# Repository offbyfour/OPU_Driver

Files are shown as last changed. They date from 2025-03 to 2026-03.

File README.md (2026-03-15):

# Blu-Ray Lithography
## Introduction
This is the project page for a lithography system based on repurposing Blu-Ray drives. The initial goal is to reach a feature size of at least 500nm (2x the Blu-ray laser spot size). As a stretch goal, we would like to also use the sled and spindle motors as high speed nano-positioners and to spin coat and cure photo-resin.

## Safety
✓ Safety goggles/glasses are absolutely necessary.
A laser dot contains a large amount of energy in such a small space, in the form of light. Your eyes are extremely sensitive to light, and a direct exposure to this very dense energy light for less than a second will blind you for life. We can prevent this by wearing a special type of light filtering glasses, somewhat like the way sunglasses work. But, sunglasses will not work as laser safety glasses. These glasses need to be coated for the correct wavelength. Do not purchase any laser safety glasses under $30, buy from an authorized and reputable seller such as survival lasers. $5 lenses from China will not be sufficient, and have been proven unsafe.

Currently Recommended: https://www.amazon.com/Tool-Klean-Safety-Glasses-Protection/dp/B081BHTJT8/ref=sr_1_5

✓ Be fully aware of what you are pointing at.
With a massive amount of light comes the heat as well. Lasers higher than Class IV (>500mW) burn certain objects very easily, lower powers do burn as well but not as intensely. Lasers like this can most definitely burn furniture such as carpet and couches, hardwood floors, curtains, walls etc. You need to make sure that you are not burning anything against your desire. If the heat build up in an object from a laser is sufficient enough, the object could be set on fire.

✓ Keep in mind of any dangerous objects/surfaces.
Look out for anything noticeably reflective/smooth such as a mirror, polished metal, or even something smooth like a desk. The last thing you want is a laser beam reflected back at you into your eye. Even with safety goggles/glasses, you should not take a chance. Something else dangerous that you need to look out for are flammable items, a high powered laser can easily ignite a match or alcohol. CAREFUL WITH WINDOWS - None are 100% transparent, and WILL reflect a solid beam back towards you, this goes for any type of glass at all. All reflected beams are also a danger and this is no exception. Windows are also a bad thing to be pointing a laser through, you don't know exactly where/what you'll hit.

__________________________________________________

Be careful with lasers, treat them like a loaded gun. It is very easy to create dangerous situations with a laser if you're not careful, be responsible and eliminate that possibility!
Source: laserpointerforums.com

## Project Status

 

Right now, the first project for this technology (Lithography Spinner V1) is in the research/idea stage. See work in progress page for details on upcoming tasks if you want to contribute.

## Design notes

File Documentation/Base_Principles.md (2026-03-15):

<details>
  <summary>STED Lithography (reaching 100nm and below)</summary>
1.STED Microscopy
	
https://www.youtube.com/watch?v=1pgpzHao1c0

2.Two-beam OBL utilizes a doughnut-shaped inhibition beam to inhibit the photopolymerization triggered by the writing beam at the doughnut ring leading to reduced feature size and improved resolution 

https://www.nature.com/articles/ncomms3061

3.Super-resolved critical dimensions in far-field I-line photolithography

https://www.spiedigitallibrary.org/journals/journal-of-micro-nanolithography-mems-and-moems/volume-18/issue-1/013505/Super-resolved-critical-dimensions-in-far-field-I-line-photolithography/10.1117/1.JMM.18.1.013505.short

4.Possible STED Architecture

Diagram of BSM. The fluorescence signal passes through multimode fiber B7 and is collimated by collimator lens B8 and narrowband emission filter B9. D1, laser diode; D2, beam splitter; D3, collimator lens; D4, dichroic filter; D5, photodiode; D6, objective lens (NA: 0.6); D7, Al-coated address pattern; B1, blue laser diode; B2, B3, beam splitters; B4, collimator lens; B5, dichroic filter; B6, 4.34 mm focal lens; B10, objective lens (NA: 0.85); B11, lens holder. B12, cover glass; B13, collimator astigmatic plate; B14, photodetector. (https://pmc.ncbi.nlm.nih.gov/articles/PMC6066758/)

</details>

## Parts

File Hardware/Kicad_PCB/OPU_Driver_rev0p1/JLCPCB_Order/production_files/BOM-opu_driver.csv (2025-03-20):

Comment | Designator | Footprint | LCSC | Quantity
1kΩ | R14,R28 | R_0402 | C11702 | 2
ESD9X3.3ST5G | D4 | SOD-923_L0.8-W0.6-LS1.0-RD | C130456 | 1
10nF | C47,C48,C49,C50,C51,C52,C53,C54,C55,C56,C57,C58,C59,C61,C72,C73 | C_0402 | C15195 | 16
TLV62569DRLR | U10,U11 | SOT-563_L1.6-W1.2-P0.50-LS1.6-BL | C163217 | 2
RC0402FR-071K8L | R27 | R0402 | C163481 | 1
0Ω | R23,R24,R25 | R_0402 | C17168 | 3
0Ω | R38,R39 | R_0603 | C21189 | 2
White | D9 | D_0603 | C2290 | 1
360kΩ | R19 | R_0603 | C23146 | 1
750kΩ | R6 | R_0603 | C23240 | 1
82kΩ | R22 | R_0603 | C23254 | 1
100Ω | R26 | R_0402 | C25076 | 1
33Ω | R44,R45,R46 | R_0402 | C25105 | 3
51Ω | R29,R30 | R_0402 | C25125 | 2
1Ω | R31,R32,R33,R34 | R_0805 | C25271 | 4
X1E0000210295 | X1 | CRYSTAL-SMD_4P-L3.2-W2.5-BL | C255930 | 1
100kΩ | R21 | R_0402 | C25741 | 1
10kΩ | R10,R20,R35,R41,R42,R43 | R_0402 | C25744 | 6
120kΩ | R18 | R_0402 | C25750 | 1
150kΩ | R5 | R_0402 | C25755 | 1
200kΩ | R1 | R_0402 | C25764 | 1
4.7kΩ | R11,R13,R15,R16,R17,R3,R4,R40,R7,R8,R9 | R_0402 | C25900 | 11
MAX1304ECM+T | U6 | TQFP-48_L7.0-W7.0-P0.50-LS9.0-BL | C2670670 | 1
GT-USB-7018 | USB1 | TYPE-C-SMD_GT-USB-7018 | C2762978 | 1
1uF | C4,C81,C90 | C_0805 | C28323 | 3
CH569W | U1 | QFN-68_L8.0-W8.0-P0.40-BL-EP5.5 | C2857462 | 1
HD3SS3220IRNHT | U2 | WQFN-30_L4.5-W2.5-P0.4-BL-EP | C2876685 | 1
DIP Switch x 2 | S1 | SW-SMD_218-2LPSTRF | C2961921 | 1
4.7uF | C100,C101,C102,C103,C104,C105,C106,C107,C108,C3,C5,C79,C80,C82,C83,C84,C85,C86,C87,C88,C89,C95,C96,C97,C98,C99 | C_1206 | C29823 | 26
Green | D7 | D_0603 | C2986059 | 1
6pF | C117 | C_0402 | C30274 | 1
100nF | C10,C109,C11,C110,C111,C112,C113,C114,C115,C116,C118,C119,C12,C120,C121,C122,C123,C124,C125,C126,C127,C128,C13,C14,C15,C16,C17,C18,C19,C20,C21,C22,C23,C24,C25,C26,C27,C28,C29,C30,C31,C32,C33,C34,C35,C36,C37,C38,C39,C40,C41,C42,C43,C44,C45,C46,C60,C62,C63,C64,C65,C67,C68,C69,C70,C74,C75,C76,C77,C78,C8,C9,C92 | C_0402 | C307331 | 73
Tactile Button, 160gf | S2 | SW-SMD_4P-L5.1-W5.1-P3.70-LS6.5-TL-2 | C318884 | 1
10pF | C6,C7,C93,C94 | C_0402 | C32949 | 4
2kΩ | R36,R37 | R_0402 | C4109 | 2
TPD1S414YZR | U3 | DSBGA-12_L1.9-W1.4-R3-C4-P0.40-TL | C411873 | 1
ZX-PM1.0-2-20PU-W | H1 | HDR-SMD_40P-P1.00-V-F-R2-C20-LS3.8 | C41369836 | 1
LM3880MF-1AA/NOPB | U13 | SOT-23-6_L2.9-W1.6-P0.95-LS2.8-BR | C486059 | 1
2.2uF | C1,C2,C66,C71,C91 | C_1206 | C50254 | 5
CR2512J1R220G | R12 | R2512 | C5381546 | 1
PMEG6010AESBYL | D5,D6 | X1SON-2_L1.0-W0.6-P0.65-RD | C552929 | 2
BLM15EX331SN1D | L1 | L0402 | C596498 | 1
NCP115CMX250TCG | U9 | XDFN-4_L1.0-W1.0-P0.65-BL-EP | C603508 | 1
ESD8004MUTAG | D1,D2,D3 | UDFN-10_L2.5-W1.0-P0.50-BL | C605399 | 3
EPC21603 | U12 | BGA-6_L1.5-W1.0-P0.50-TL | C6191277 | 1
TPIC2010RDFDRG4 | U8 | HTSSOP-56_L14.0-W6.0-P0.50-LS8.1-BL-EP | C702134 | 1
MAX40025CAWT+T | U5 | WLP-6_L1.2-W0.8-R2-C3-P0.40-TL_MAX40111ANT | C7451830 | 1
2N7002 | Q1,Q2 | Q_SOT-23 | C8545 | 2
LQM21PN2R2NGCD | L2,L3 | L0805 | C86089 | 2
TestPoint | TP11 | TestPoint_Pad_D1.0mm |  | 1
LMK3H0102A014RERT | U7 | TQFN16_RER_TEX |  | 1
TestPoint | TP6 | TestPoint_Pad_D1.0mm |  | 1
TestPoint | TP8 | TestPoint_Pad_D1.0mm |  | 1
TestPoint | TP10 | TestPoint_Pad_D1.0mm |  | 1
TestPoint | TP7 | TestPoint_Pad_D1.0mm |  | 1
TestPoint | TP9 | TestPoint_Pad_D1.0mm |  | 1
LFE5U-25F-8MG285C | U4 | csBGA285 |  | 1
TestPoint | TP1 | TestPoint_Pad_D1.0mm |  | 1
TestPoint | TP5 | TestPoint_Pad_D1.0mm |  | 1
TestPoint | TP4 | TestPoint_Pad_D1.0mm |  | 1
TestPoint | TP2 | TestPoint_Pad_D1.0mm |  | 1
TestPoint | TP3 | TestPoint_Pad_D1.0mm |  | 1

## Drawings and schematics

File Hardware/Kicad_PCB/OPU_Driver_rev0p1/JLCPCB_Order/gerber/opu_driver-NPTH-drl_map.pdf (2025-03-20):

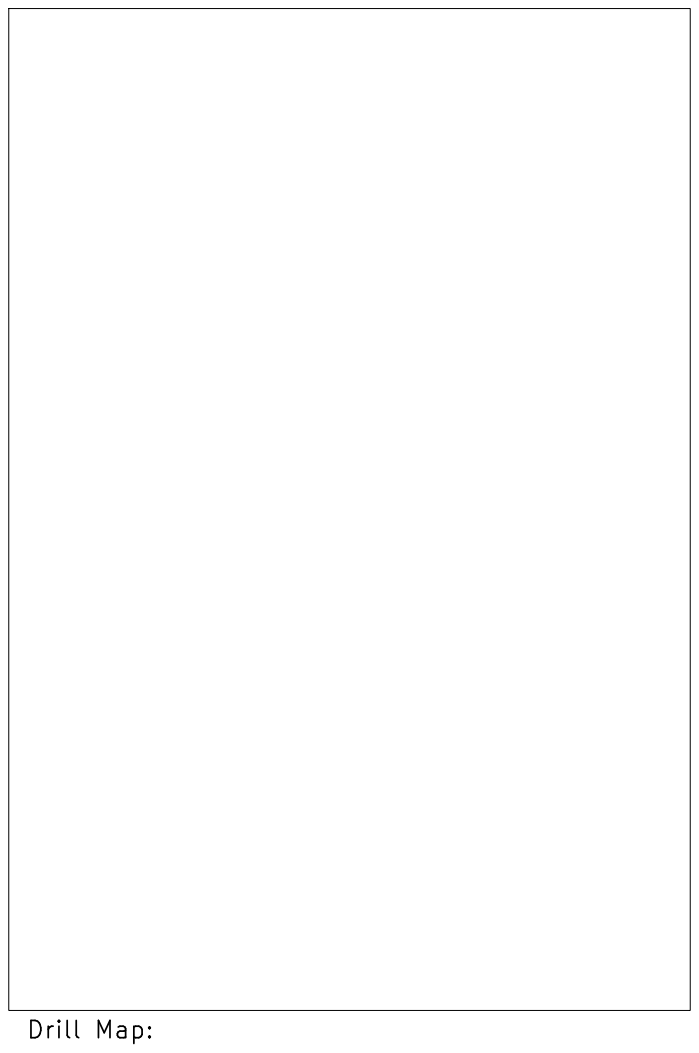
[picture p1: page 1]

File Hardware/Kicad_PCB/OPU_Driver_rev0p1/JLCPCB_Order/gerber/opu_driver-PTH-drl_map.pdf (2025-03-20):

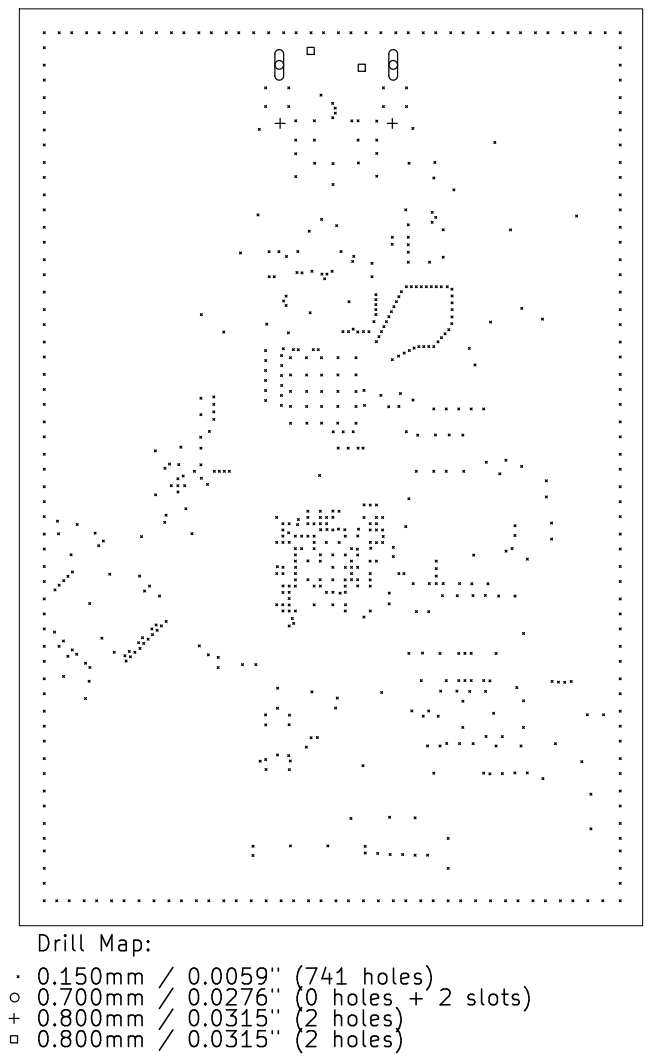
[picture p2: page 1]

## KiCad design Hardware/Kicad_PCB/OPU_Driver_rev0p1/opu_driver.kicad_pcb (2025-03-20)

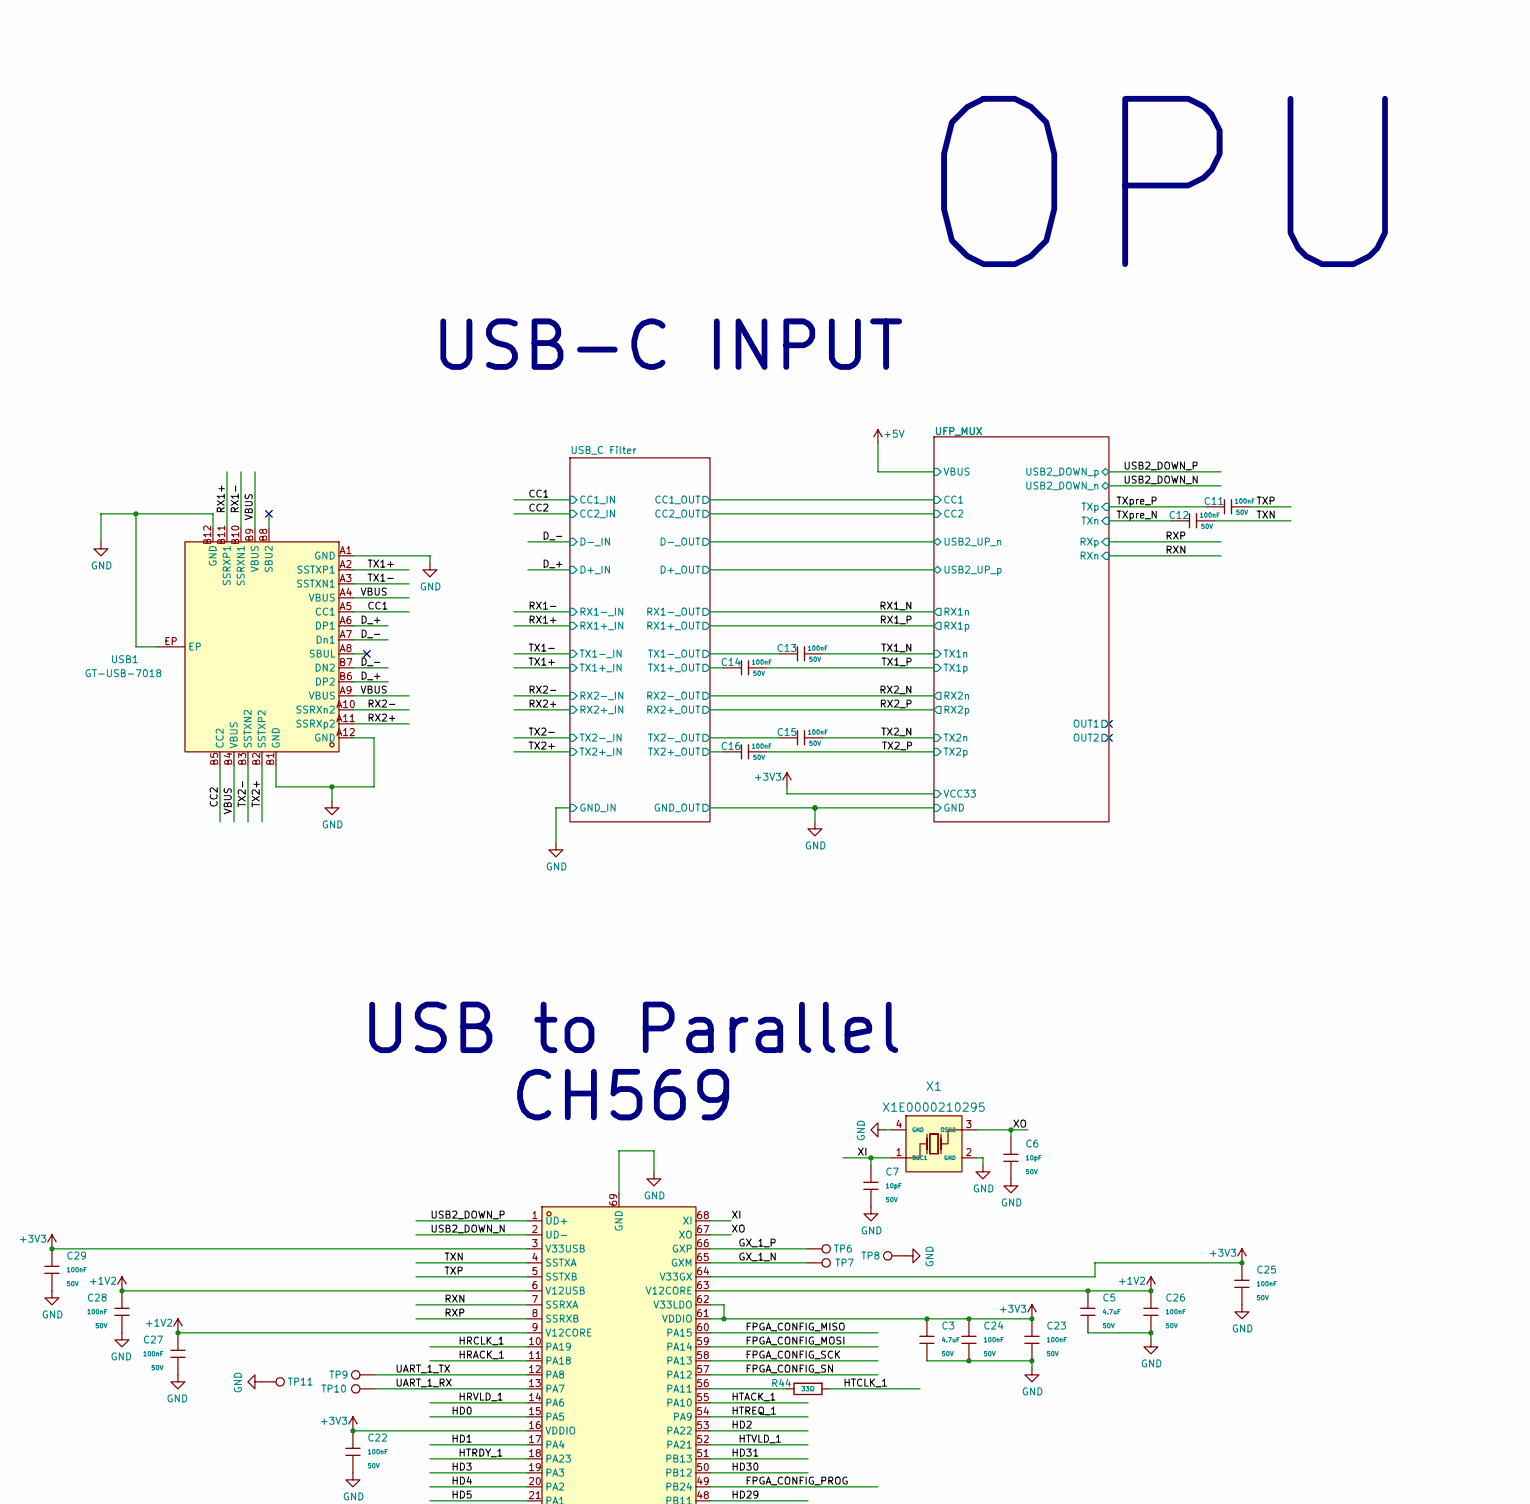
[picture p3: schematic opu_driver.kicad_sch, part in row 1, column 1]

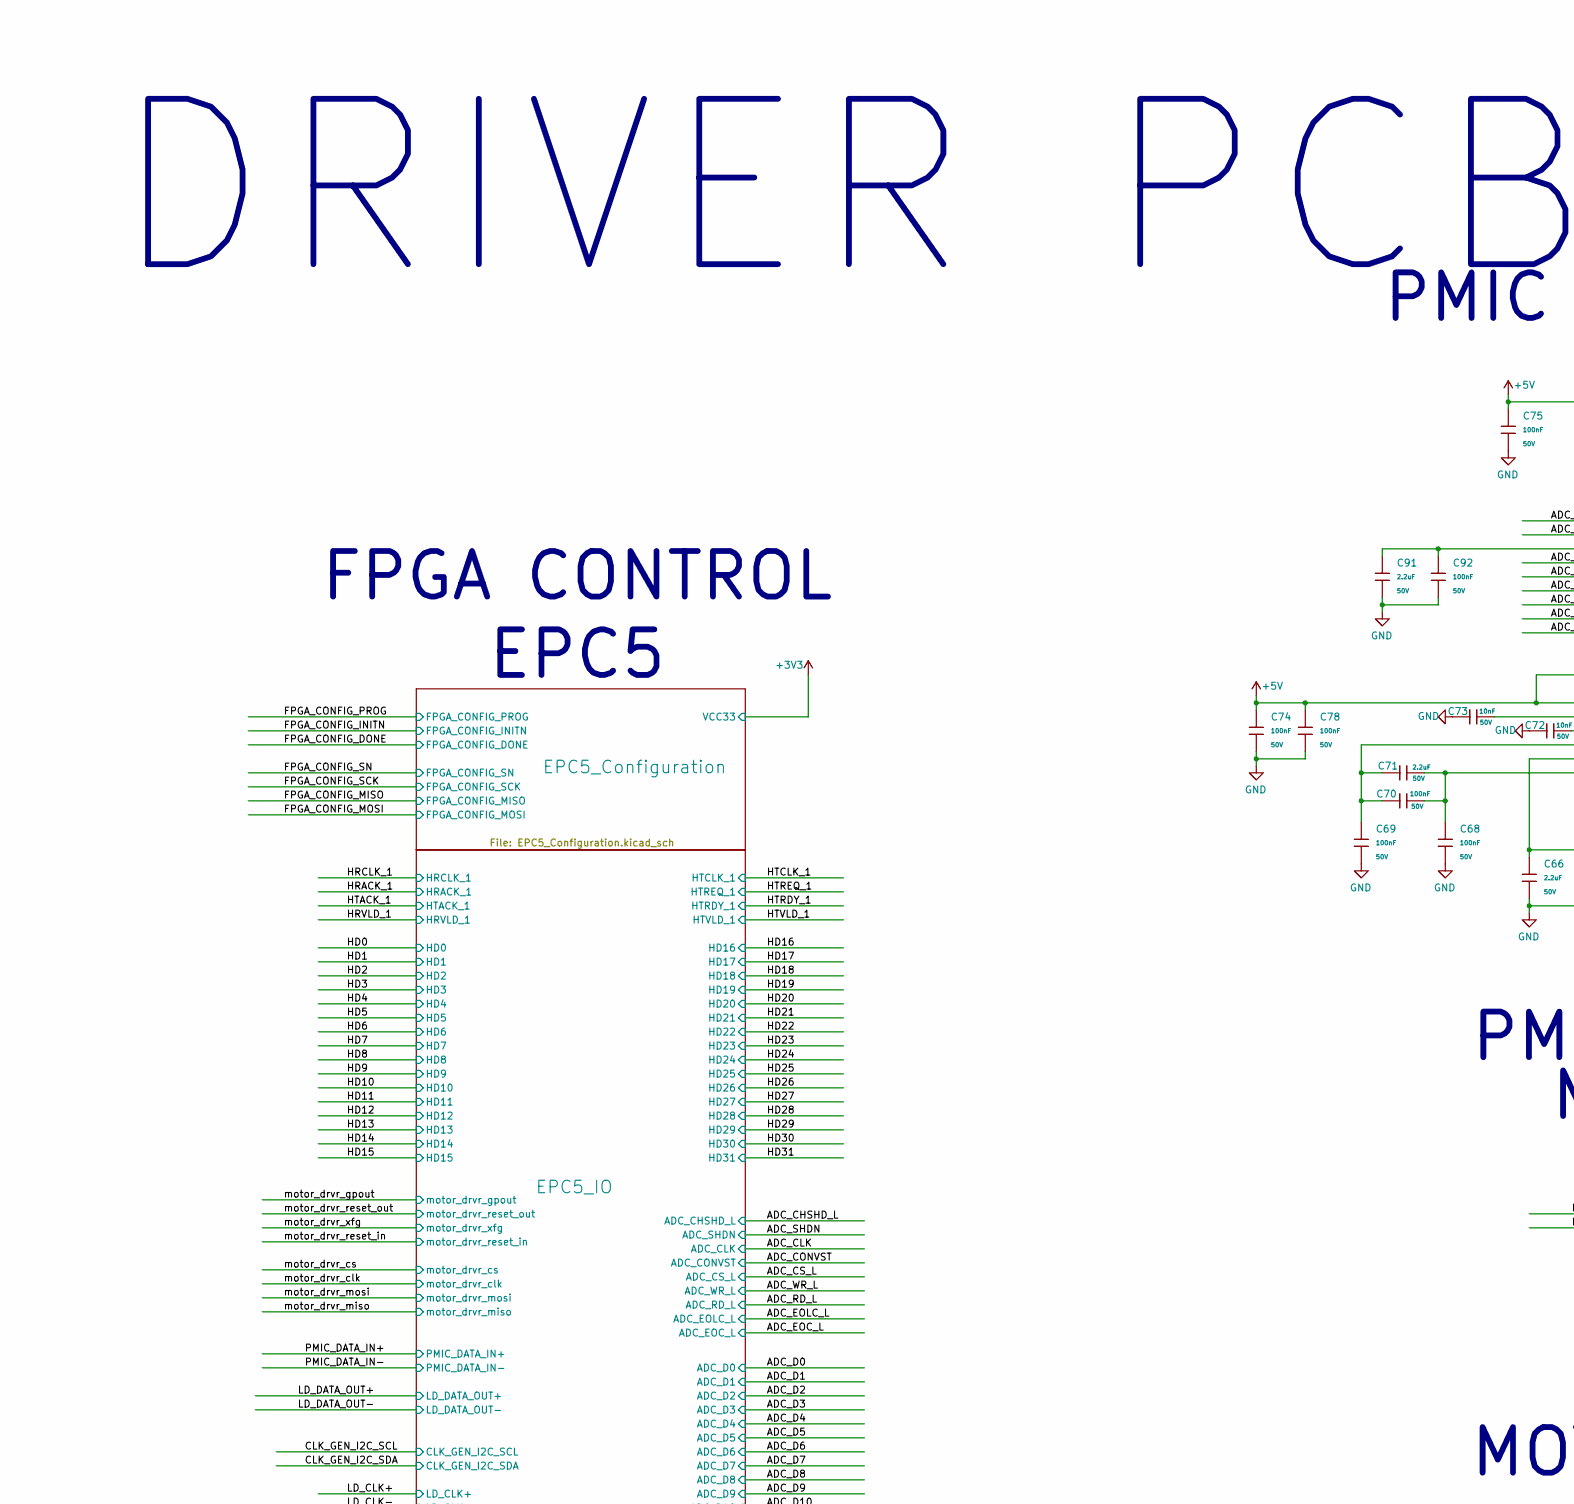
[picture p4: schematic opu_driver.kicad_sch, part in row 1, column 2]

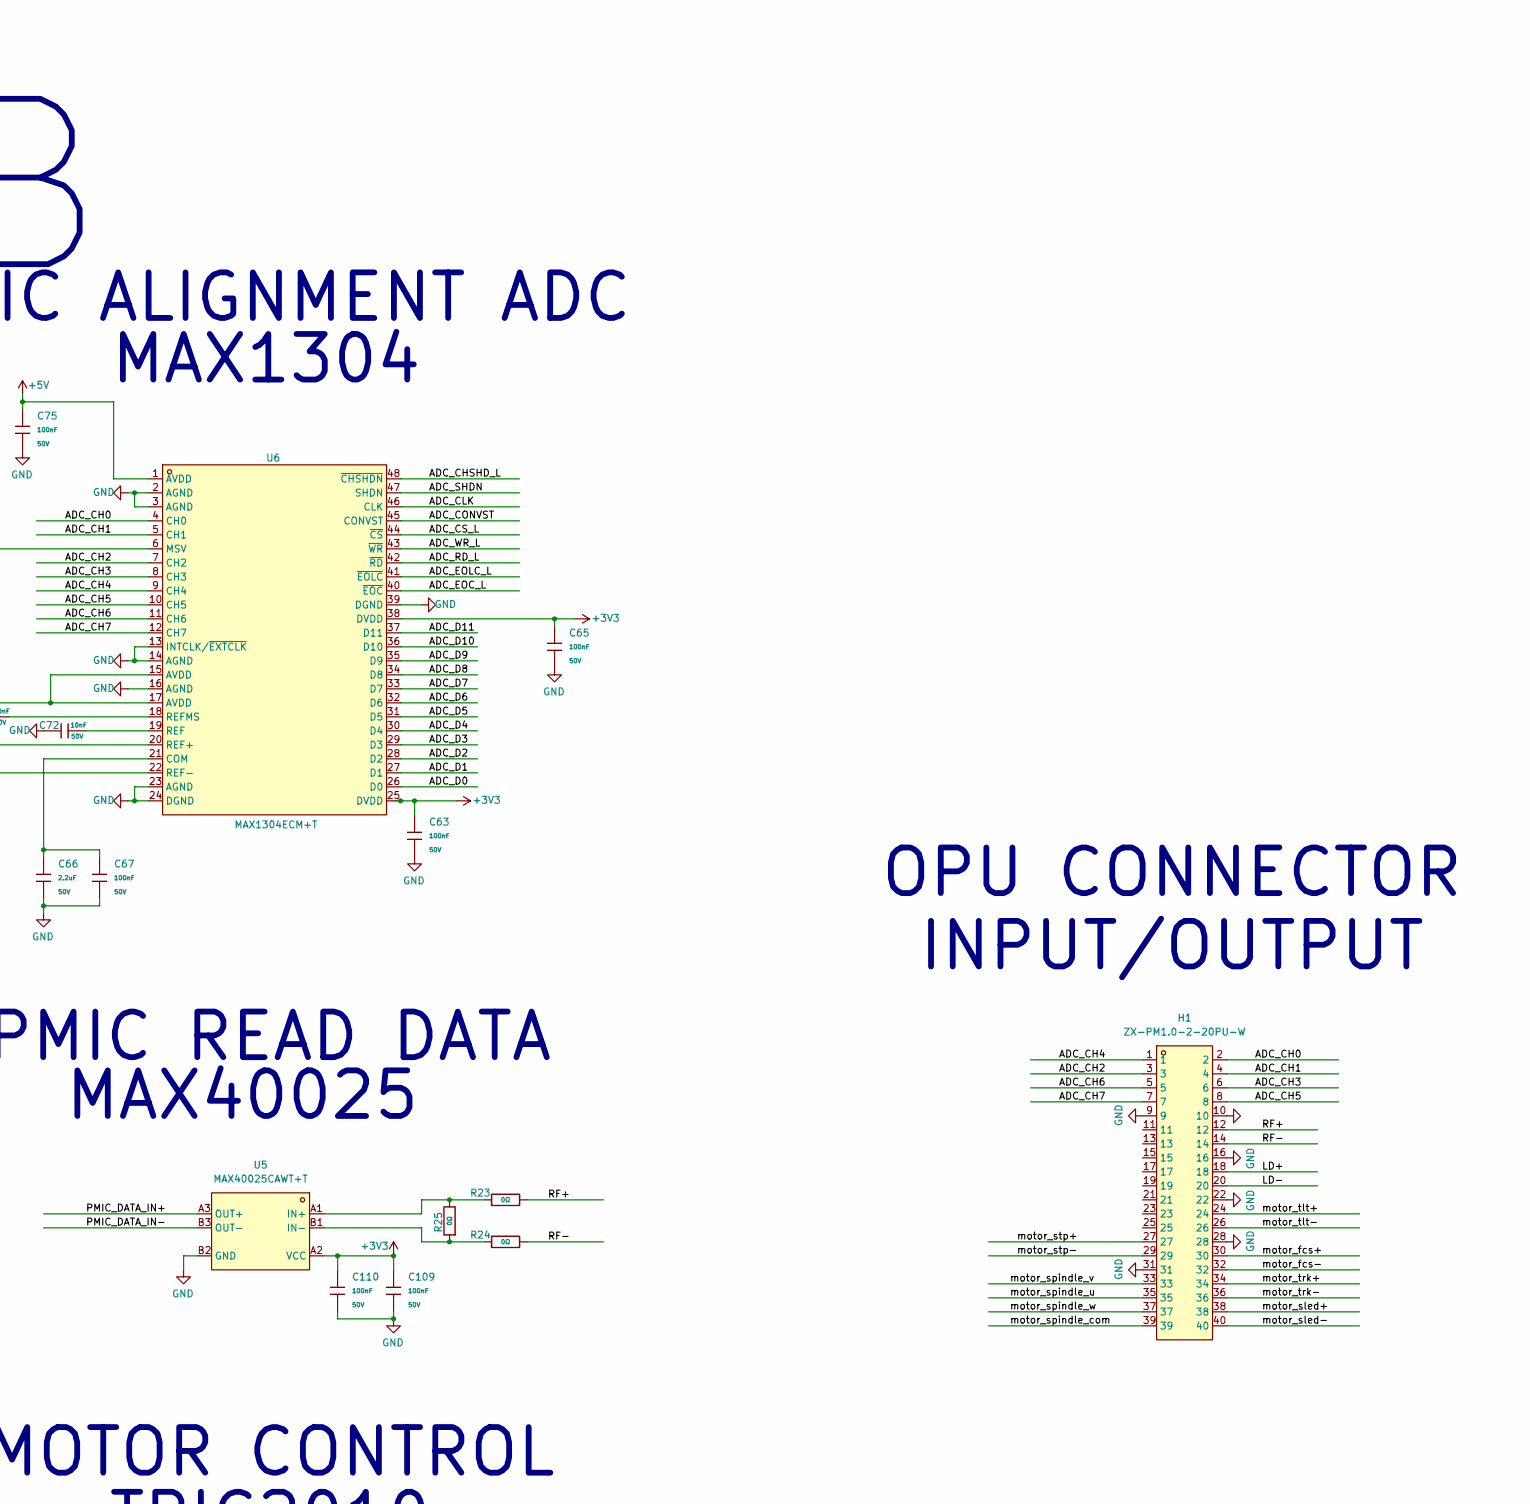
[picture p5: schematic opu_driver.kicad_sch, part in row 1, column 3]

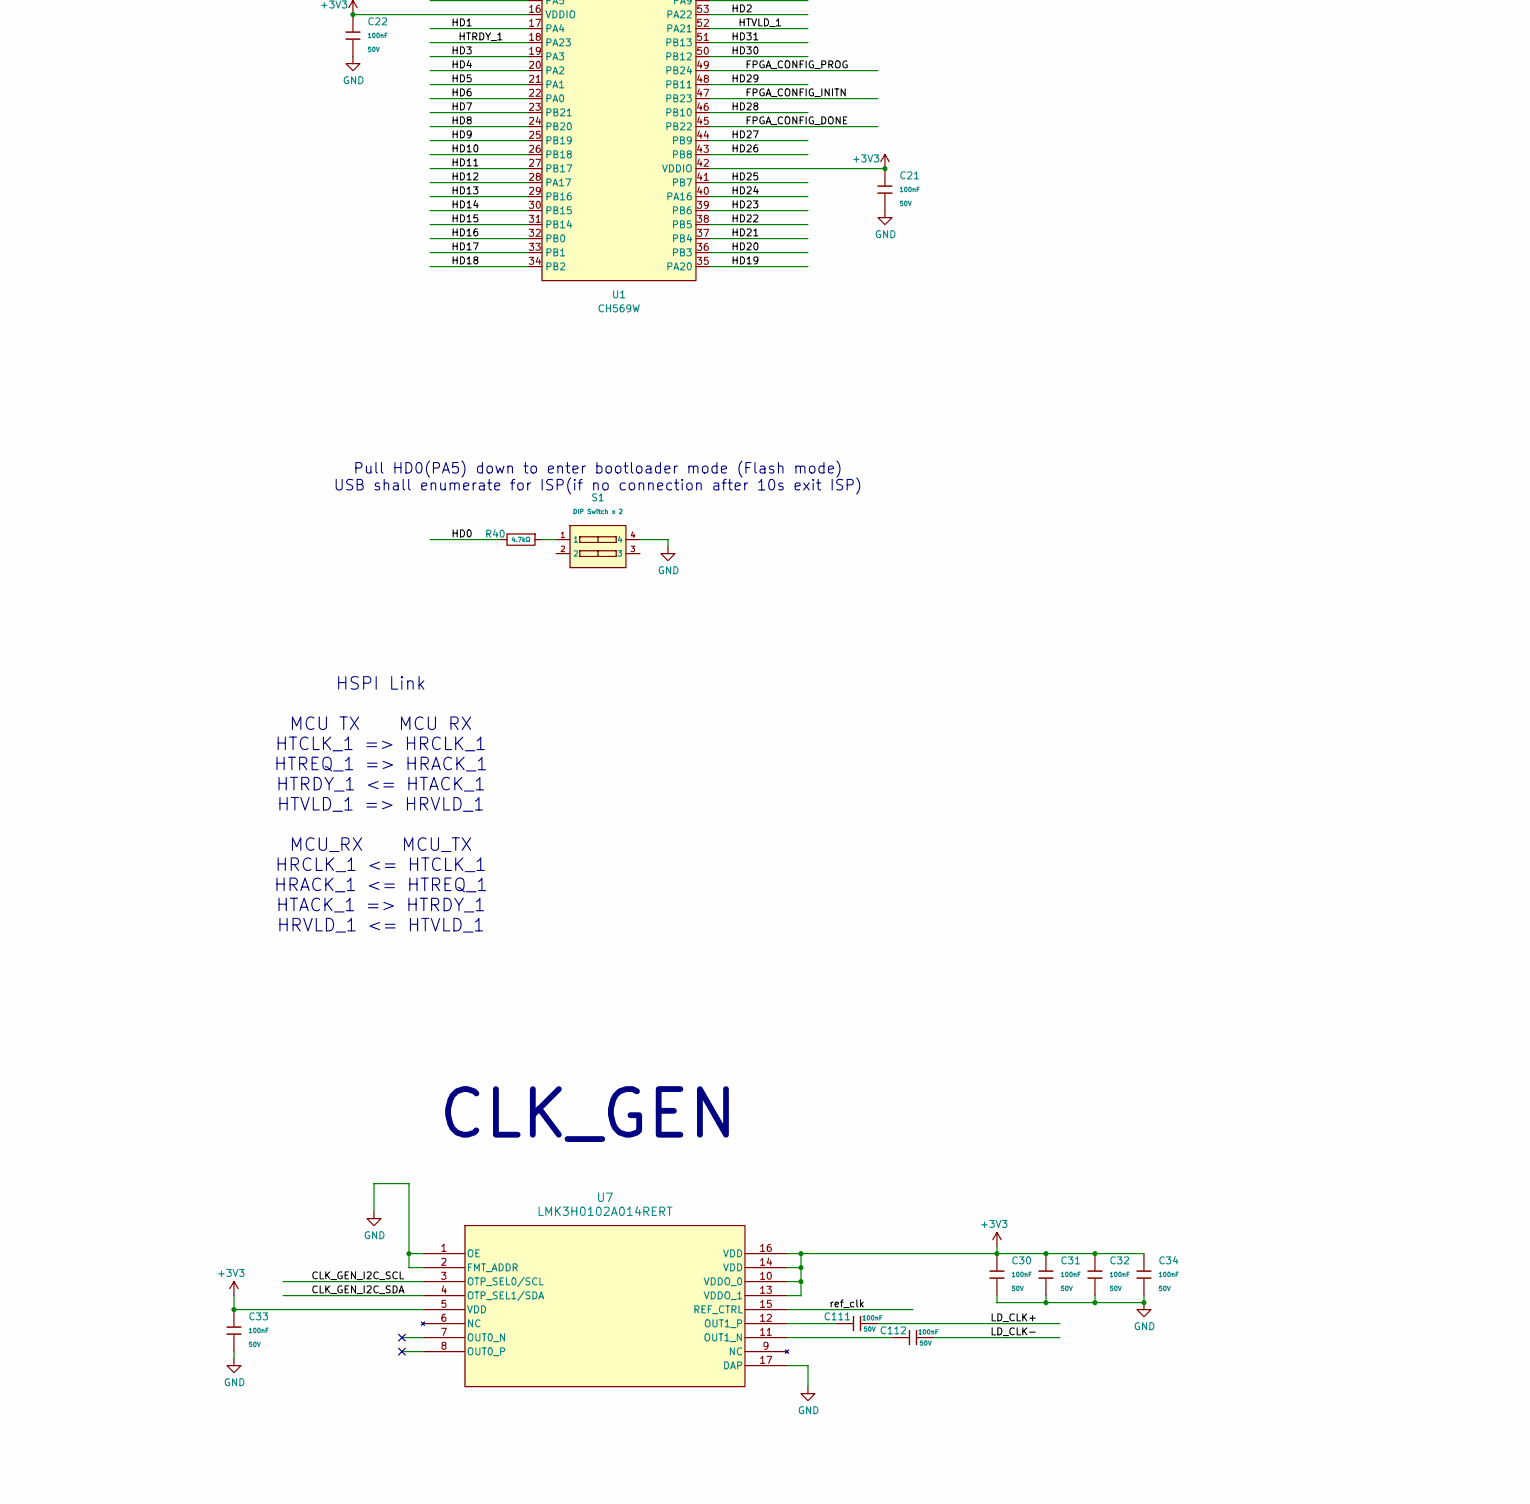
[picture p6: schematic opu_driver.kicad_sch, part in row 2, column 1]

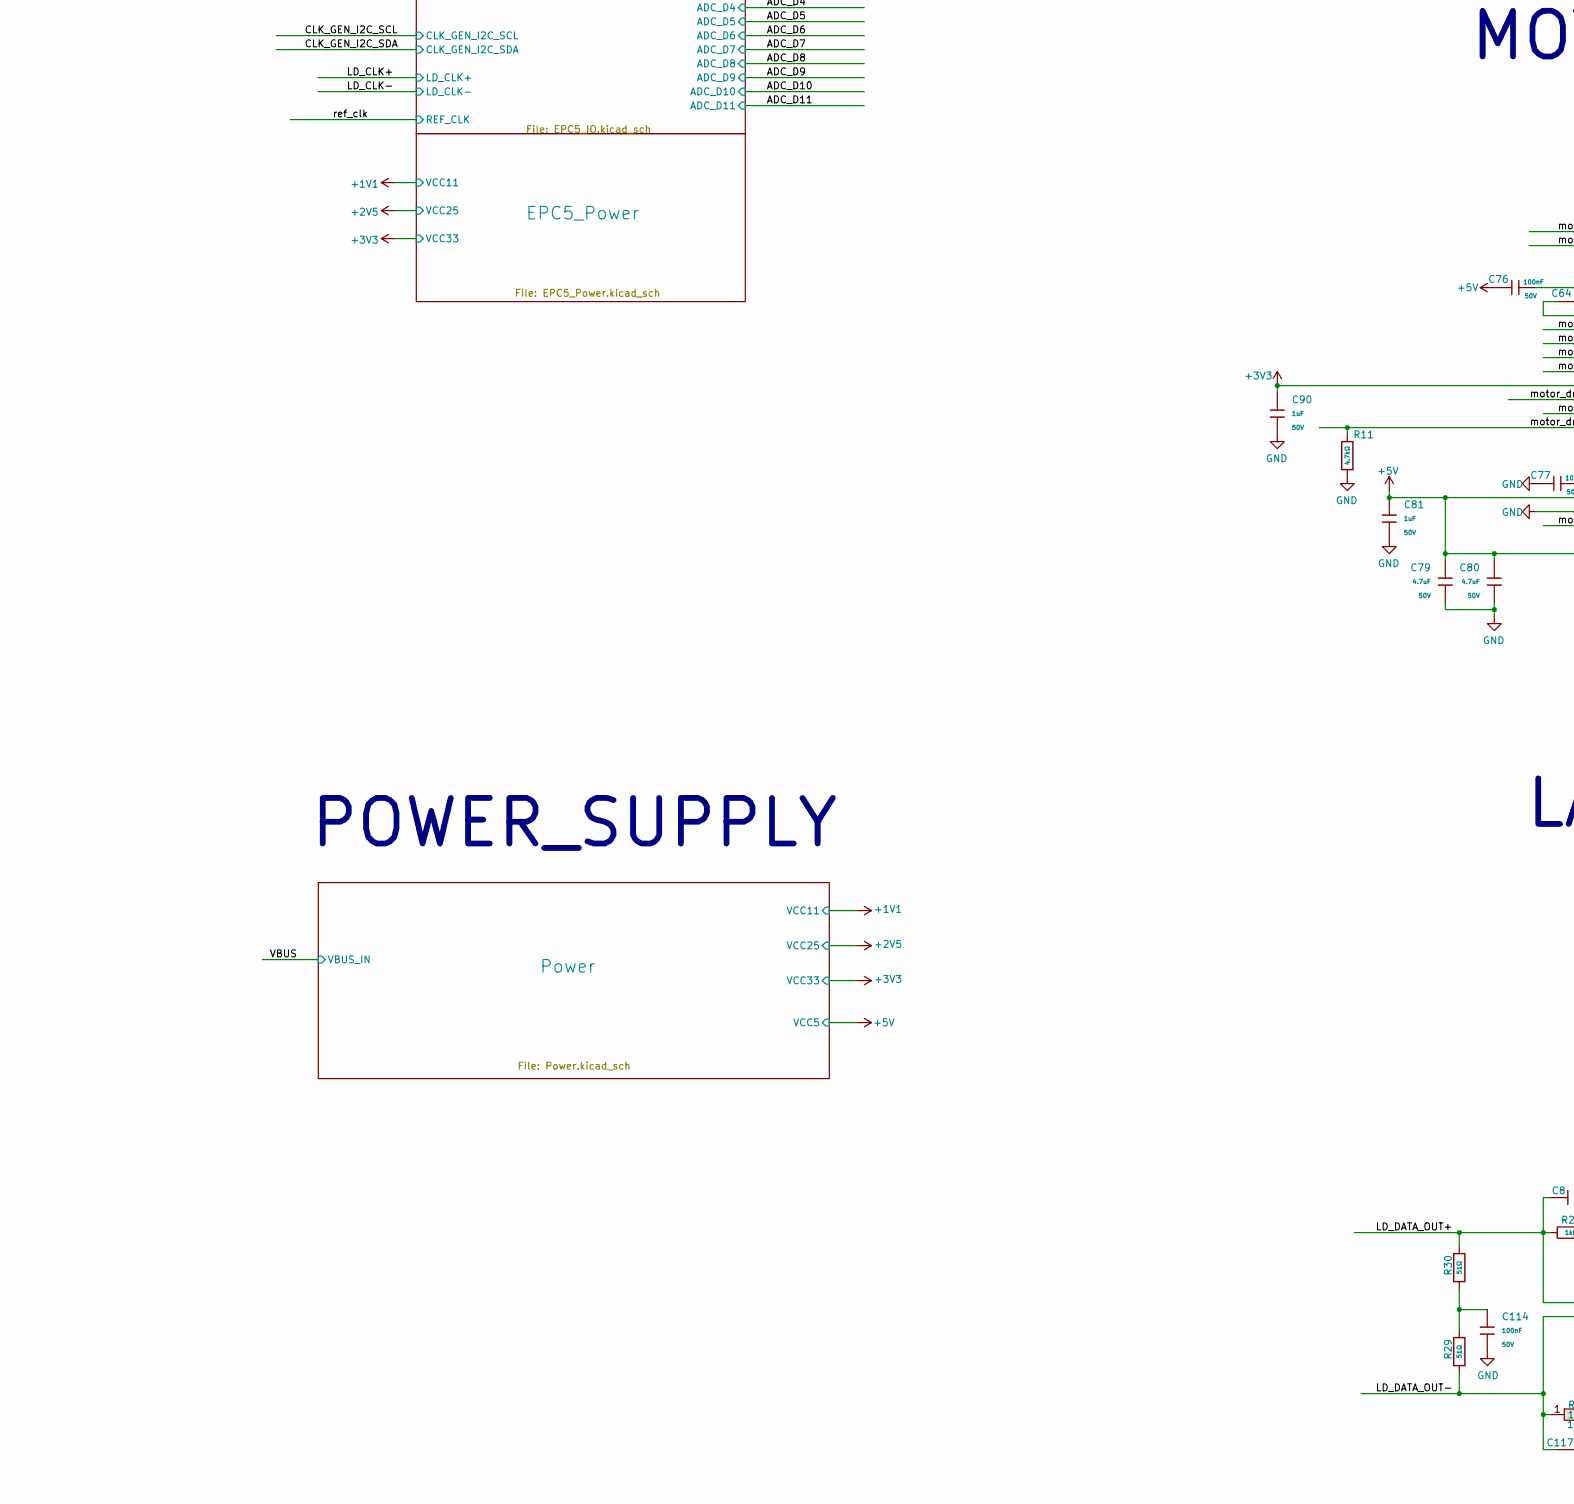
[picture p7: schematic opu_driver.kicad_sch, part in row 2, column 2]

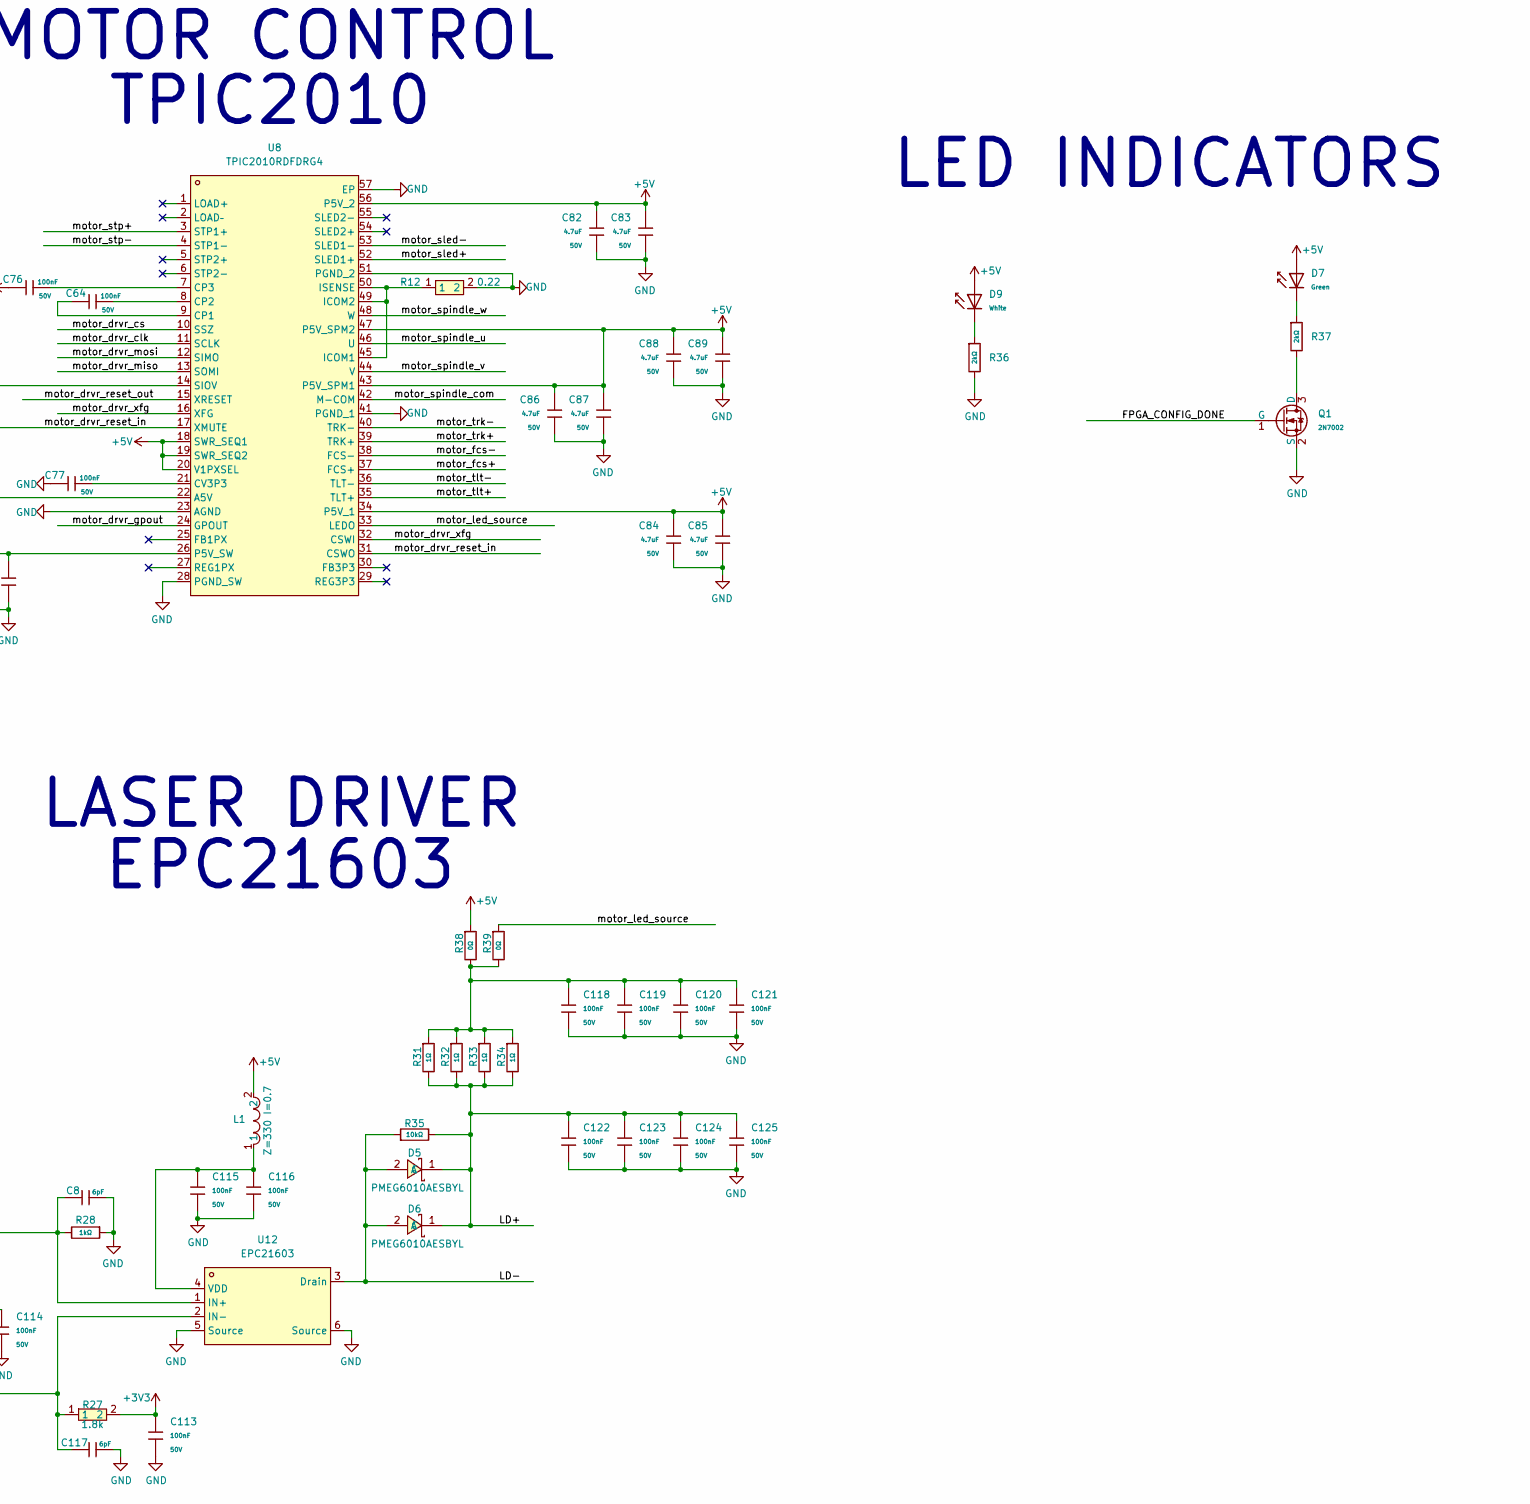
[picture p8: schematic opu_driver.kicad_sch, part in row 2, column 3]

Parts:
C3, C5, C79, C80, C82, C83, C84, C85, C86, C87, C88, C89: 4.7uF; C_1206; Voltage Rated 50V; Tolerance ±10%; Part 1206B475K500NT; LCSC C29823
C6, C7: 10pF; C_0402; Voltage Rated 50V; Tolerance ±5%; Part CL05C100JB5NNNC; LCSC C32949
C8, C117: 6pF; C_0402; Part 0402CG6R0C500NT (SMT业务专用); LCSC C30274
C11, C12, C13, C14, C15, C16, C21, C22, C23, C24, C25, C26, C27, C28, C29, C30, C31, C32, C33, C34, C63, C64, C65, C67, C68, C69, C70, C74, C75, C76, C77, C78, C92, C109, C110, C111, C112, C113, C114, C115, C116, C118, C119, C120, C121, C122, C123, C124, C125: 100nF; C_0402; Voltage Rated 50V; Tolerance ±10%; Part CL05B104KB54PNC; LCSC C307331
C66, C71, C91: 2.2uF; C_1206; Voltage Rated 50V; Tolerance ±10%; Part CL31B225KBHNNNE; LCSC C50254
C72, C73: 10nF; C_0402; Voltage Rated 50V; Tolerance ±10%; Part CL05B103KB5NNNC; LCSC C15195
C81, C90: 1uF; C_0805; Voltage Rated 50V; Tolerance ±10%; Part CL21B105KBFNNNE; LCSC C28323
D5, D6: PMEG6010AESBYL; X1SON-2_L1.0-W0.6-P0.65-RD; LCSC Part C552929
D7: Green; D_0603; Part 19-217/GHC-YR1S2/6T; LCSC C2986059
D9: White; D_0603; Part KT-0603W; LCSC C2290
H1: ZX-PM1.0-2-20PU-W; HDR-SMD_40P-P1.00-V-F-R2-C20-LS3.8; LCSC Part C41369836
L1: BLM15EX331SN1D; L0402; LCSC Part C596498
Q1: 2N7002; Q_SOT-23; Part 2N7002; LCSC C8545
R11, R40: 4.7kΩ; R_0402; Overload Voltage (Max) 50V; Tolerance ±1%; Part 0402WGF4701TCE; LCSC C25900
R12: CR2512J1R220G; R2512; LCSC Part C5381546
R23, R24, R25: 0Ω; R_0402; Overload Voltage (Max) 50V; Tolerance ±1%; Part 0402WGF0000TCE; LCSC C17168
R27: RC0402FR-071K8L; R0402; LCSC Part C163481
R28: 1kΩ; R_0402; Overload Voltage (Max) 50V; Tolerance ±1%; Part 0402WGF1001TCE; LCSC C11702
R29, R30: 51Ω; R_0402; Overload Voltage (Max) 50V; Tolerance ±1%; Part 0402WGF510JTCE; LCSC C25125
R31, R32, R33, R34: 1Ω; R_0805; Overload Voltage (Max) 150V; Tolerance ±1%; Part 0805W8F100KT5E; LCSC C25271
R35: 10kΩ; R_0402; Overload Voltage (Max) 50V; Tolerance ±1%; Part 0402WGF1002TCE; LCSC C25744
R36, R37: 2kΩ; R_0402; Overload Voltage (Max) 50V; Tolerance ±1%; Part 0402WGF2001TCE; LCSC C4109
R38, R39: 0Ω; R_0603; Overload Voltage (Max) 75V; Tolerance ±1%; Part 0603WAF0000T5E; LCSC C21189
R44: 33Ω; R_0402; Overload Voltage (Max) 50V; Tolerance ±1%; Part 0402WGF330JTCE; LCSC C25105
S1: DIP Switch x 2; SW-SMD_218-2LPSTRF; Current Rating 25mA; Voltage Rating 24V; Part 218-2LPSTR; LCSC C2961921
TP6, TP7, TP8, TP9, TP10, TP11: TestPoint; TestPoint_Pad_D1.0mm
U1: CH569W; QFN-68_L8.0-W8.0-P0.40-BL-EP5.5; LCSC Part C2857462
U5: MAX40025CAWT+T; WLP-6_L1.2-W0.8-R2-C3-P0.40-TL_MAX40111ANT; LCSC Part C7451830
U6: MAX1304ECM+T; TQFP-48_L7.0-W7.0-P0.50-LS9.0-BL; LCSC Part C2670670
U7: LMK3H0102A014RERT; TQFN16_RER_TEX
U8: TPIC2010RDFDRG4; HTSSOP-56_L14.0-W6.0-P0.50-LS8.1-BL-EP; LCSC Part C702134
U12: EPC21603; BGA-6_L1.5-W1.0-P0.50-TL; LCSC Part C6191277
USB1: GT-USB-7018; TYPE-C-SMD_GT-USB-7018; LCSC Part C2762978
X1: X1E0000210295; CRYSTAL-SMD_4P-L3.2-W2.5-BL; LCSC Part C255930

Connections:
+1V2: C5.1, C26.1, C27.1, C28.1, U1.6 (V12USB), U1.9 (V12CORE), U1.63 (V12CORE)
+3V3: C3.1, C21.1, C22.1, C23.1, C24.1, C25.1, C29.1, C30.1, C31.1, C32.1, C33.1, C34.1, C63.1, C65.1, C90.1, C109.1, C110.1, C113.1, R27.2, U1.3 (V33USB), U1.16 (VDDIO), U1.42 (VDDIO), U1.61 (VDDIO), U1.62 (V33LDO), U1.64 (V33GX), U5.A2 (VCC), U6.25 (DVDD), U6.38 (DVDD), U7.5 (VDD), U7.10 (VDDO_0), U7.13 (VDDO_1), U7.14 (VDD), U7.16 (VDD), U8.14 (SIOV); also elsewhere on the board
/ADC_CH0: H1.2, U6.4 (CH0)
/ADC_CH1: H1.4, U6.5 (CH1)
/ADC_CH2: H1.3, U6.7 (CH2)
/ADC_CH3: H1.6, U6.8 (CH3)
/ADC_CH4: H1.1, U6.9 (CH4)
/ADC_CH5: H1.8, U6.10 (CH5)
/ADC_CH6: H1.5, U6.11 (CH6)
/ADC_CH7: H1.7, U6.12 (CH7)
/ADC_CHSHD_L: U6.48 (~CHSHDN); also elsewhere on the board
/ADC_CLK: U6.46 (CLK); also elsewhere on the board
/ADC_CONVST: U6.45 (CONVST); also elsewhere on the board
/ADC_CS_L: U6.44 (~CS); also elsewhere on the board
/ADC_D0: U6.26 (D0); also elsewhere on the board
/ADC_D1: U6.27 (D1); also elsewhere on the board
/ADC_D2: U6.28 (D2); also elsewhere on the board
/ADC_D3: U6.29 (D3); also elsewhere on the board
/ADC_D4: U6.30 (D4); also elsewhere on the board
/ADC_D5: U6.31 (D5); also elsewhere on the board
/ADC_D6: U6.32 (D6); also elsewhere on the board
/ADC_D7: U6.33 (D7); also elsewhere on the board
/ADC_D8: U6.34 (D8); also elsewhere on the board
/ADC_D9: U6.35 (D9); also elsewhere on the board
/ADC_D10: U6.36 (D10); also elsewhere on the board
/ADC_D11: U6.37 (D11); also elsewhere on the board
/ADC_EOC_L: U6.40 (~EOC); also elsewhere on the board
/ADC_EOLC_L: U6.41 (~EOLC); also elsewhere on the board
/ADC_RD_L: U6.42 (~RD); also elsewhere on the board
/ADC_SHDN: U6.47 (SHDN); also elsewhere on the board
/ADC_WR_L: U6.43 (~WR); also elsewhere on the board
/CC1: USB1.A5 (CC1); also elsewhere on the board
/CC2: USB1.B5 (CC2); also elsewhere on the board
/CLK_GEN_I2C_SCL: U7.3 (OTP_SEL0/SCL); also elsewhere on the board
/CLK_GEN_I2C_SDA: U7.4 (OTP_SEL1/SDA); also elsewhere on the board
/D_+: U1.1 (UD+), USB1.A6 (DP1), USB1.B6 (DP2); also elsewhere on the board
/D_-: U1.2 (UD-), USB1.A7 (Dn1), USB1.B7 (DN2); also elsewhere on the board
/FPGA_CONFIG_DONE: Q1.1 (G), U1.45 (PB22); also elsewhere on the board
/FPGA_CONFIG_INITN: U1.47 (PB23); also elsewhere on the board
/FPGA_CONFIG_MISO: U1.60 (PA15); also elsewhere on the board
/FPGA_CONFIG_MOSI: U1.59 (PA14); also elsewhere on the board
/FPGA_CONFIG_PROG: U1.49 (PB24); also elsewhere on the board
/FPGA_CONFIG_SCK: U1.58 (PA13); also elsewhere on the board
/FPGA_CONFIG_SN: U1.57 (PA12); also elsewhere on the board
/GX_1_N: TP7.1, U1.65 (GXM)
/GX_1_P: TP6.1, U1.66 (GXP)
/HD0: R40.2, U1.15 (PA5); also elsewhere on the board
/HD1: U1.17 (PA4); also elsewhere on the board
/HD2: U1.53 (PA22); also elsewhere on the board
/HD3: U1.19 (PA3); also elsewhere on the board
/HD4: U1.20 (PA2); also elsewhere on the board
/HD5: U1.21 (PA1); also elsewhere on the board
/HD6: U1.22 (PA0); also elsewhere on the board
/HD7: U1.23 (PB21); also elsewhere on the board
/HD8: U1.24 (PB20); also elsewhere on the board
/HD9: U1.25 (PB19); also elsewhere on the board
/HD10: U1.26 (PB18); also elsewhere on the board
/HD11: U1.27 (PB17); also elsewhere on the board
/HD12: U1.28 (PA17); also elsewhere on the board
/HD13: U1.29 (PB16); also elsewhere on the board
/HD14: U1.30 (PB15); also elsewhere on the board
/HD15: U1.31 (PB14); also elsewhere on the board
/HD16: U1.32 (PB0); also elsewhere on the board
/HD17: U1.33 (PB1); also elsewhere on the board
/HD18: U1.34 (PB2); also elsewhere on the board
/HD19: U1.35 (PA20); also elsewhere on the board
/HD20: U1.36 (PB3); also elsewhere on the board
/HD21: U1.37 (PB4); also elsewhere on the board
/HD22: U1.38 (PB5); also elsewhere on the board
/HD23: U1.39 (PB6); also elsewhere on the board
/HD24: U1.40 (PA16); also elsewhere on the board
/HD25: U1.41 (PB7); also elsewhere on the board
/HD26: U1.43 (PB8); also elsewhere on the board
/HD27: U1.44 (PB9); also elsewhere on the board
/HD28: U1.46 (PB10); also elsewhere on the board
/HD29: U1.48 (PB11); also elsewhere on the board
/HD30: U1.50 (PB12); also elsewhere on the board
/HD31: U1.51 (PB13); also elsewhere on the board
/HRACK_1: U1.11 (PA18); also elsewhere on the board
/HRCLK_1: U1.10 (PA19); also elsewhere on the board
/HRVLD_1: U1.14 (PA6); also elsewhere on the board
/HTACK_1: U1.55 (PA10); also elsewhere on the board
/HTCLK_1: R44.1; also elsewhere on the board
/HTRDY_1: U1.18 (PA23); also elsewhere on the board
/HTREQ_1: U1.54 (PA9); also elsewhere on the board
/HTVLD_1: U1.52 (PA21); also elsewhere on the board
/LD+: C122.1, C123.1, C124.1, C125.1, D5.1 (C), D6.1 (C), H1.18, R31.2, R32.2, R33.2, R34.2, R35.2
/LD-: D5.2 (A), D6.2 (A), H1.20, R35.1, U12.3 (Drain)
/LD_CLK+: C111.2; also elsewhere on the board
/LD_CLK-: C112.2; also elsewhere on the board
/LD_DATA_OUT+: C8.1, R28.2, R30.1, U12.1 (IN+); also elsewhere on the board
/LD_DATA_OUT-: C117.1, R27.1, R29.2, U12.2 (IN-); also elsewhere on the board
/PMIC_DATA_IN+: U5.A3 (OUT+); also elsewhere on the board
/PMIC_DATA_IN-: U5.B3 (OUT-); also elsewhere on the board
/RF+: H1.12, R23.2
/RF-: H1.14, R24.2
/RX1+: USB1.B11 (SSRXP1); also elsewhere on the board
/RX1-: USB1.B10 (SSRXN1); also elsewhere on the board
/RX2+: USB1.A11 (SSRXp2); also elsewhere on the board
/RX2-: USB1.A10 (SSRXn2); also elsewhere on the board
/RXN: U1.7 (SSRXA); also elsewhere on the board
/RXP: U1.8 (SSRXB); also elsewhere on the board
/TX1+: C14.2, USB1.A2 (SSTXP1); also elsewhere on the board
/TX1-: C13.2, USB1.A3 (SSTXN1); also elsewhere on the board
/TX1_N: C13.1; also elsewhere on the board
/TX1_P: C14.1; also elsewhere on the board
/TX2+: C16.2, USB1.B2 (SSTXP2); also elsewhere on the board
/TX2-: C15.2, USB1.B3 (SSTXN2); also elsewhere on the board
/TX2_N: C15.1; also elsewhere on the board
/TX2_P: C16.1; also elsewhere on the board
/TXN: C12.1, U1.4 (SSTXA)
/TXP: C11.1, U1.5 (SSTXB)
/TXpre_N: C12.2; also elsewhere on the board
/TXpre_P: C11.2; also elsewhere on the board
/UART_1_RX: TP10.1, U1.13 (PA7)
/UART_1_TX: TP9.1, U1.12 (PA8)
/VBUS: USB1.A4 (VBUS), USB1.A9 (VBUS), USB1.B4 (VBUS), USB1.B9 (VBUS); also elsewhere on the board
/XO: C6.1, U1.67 (XO), X1.3 (OSC2)
/motor_drvr_clk: U8.11 (SCLK); also elsewhere on the board
/motor_drvr_cs: U8.10 (SSZ); also elsewhere on the board
/motor_drvr_gpout: U8.24 (GPOUT); also elsewhere on the board
/motor_drvr_miso: U8.13 (SOMI); also elsewhere on the board
/motor_drvr_mosi: U8.12 (SIMO); also elsewhere on the board
/motor_drvr_reset_in: R11.1, U8.17 (XMUTE), U8.31 (CSWO); also elsewhere on the board
/motor_drvr_reset_out: U8.15 (XRESET); also elsewhere on the board
/motor_drvr_xfg: U8.16 (XFG), U8.32 (CSWI); also elsewhere on the board
/motor_fcs+: H1.30, U8.37 (FCS+)
/motor_fcs-: H1.32, U8.38 (FCS-)
/motor_led_source: R39.1, U8.33 (LEDO)
/motor_sled+: H1.38, U8.52 (SLED1+)
/motor_sled-: H1.40, U8.53 (SLED1-)
/motor_spindle_com: H1.39, U8.42 (M-COM)
/motor_spindle_u: H1.35, U8.46 (U)
/motor_spindle_v: H1.33, U8.44 (V)
/motor_spindle_w: H1.37, U8.48 (W)
/motor_stp+: H1.27, U8.3 (STP1+)
/motor_stp-: H1.29, U8.4 (STP1-)
/motor_tlt+: H1.24, U8.35 (TLT+)
/motor_tlt-: H1.26, U8.36 (TLT-)
/motor_trk+: H1.34, U8.39 (TRK+)
/motor_trk-: H1.36, U8.40 (TRK-)
/ref_clk: U7.15 (REF_CTRL); also elsewhere on the board
GND: C3.2, C5.2, C6.2, C7.2, C8.2, C21.2, C22.2, C23.2, C24.2, C25.2, C26.2, C27.2, C28.2, C29.2, C30.2, C31.2, C32.2, C33.2, C34.2, C63.2, C65.2, C66.2, C67.2, C68.2, C69.2, C72.2, C73.2, C74.2, C75.2, C77.2, C78.2, C79.2, C80.2, C81.2, C82.2, C83.2, C84.2, C85.2, C86.2, C87.2, C88.2, C89.2, C90.2, C91.2, C92.2, C109.2, C110.2, C113.2, C114.2, C115.2, C116.2, C117.2, C118.2, C119.2, C120.2, C121.2, C122.2, C123.2, C124.2, C125.2, H1.9, H1.10, H1.16, H1.22, H1.28, H1.31, Q1.2 (S), R11.2, R12.2, R28.1, R36.2, S1.4, TP8.1, TP11.1, U1.69 (GND), U5.B2 (GND), U6.2 (AGND), U6.3 (AGND), U6.13 (INTCLK/~EXTCLK), U6.14 (AGND), U6.16 (AGND), U6.23 (AGND), U6.24 (DGND), U6.39 (DGND), U7.1 (OE), U7.2 (FMT_ADDR), U7.17 (DAP), U8.23 (AGND), U8.28 (PGND_SW), U8.41 (PGND_1), U8.51 (PGND_2), U8.57 (EP), U12.5 (Source), U12.6 (Source), USB1.A1 (GND), USB1.A12 (GND), USB1.B1 (GND), USB1.B12 (GND), USB1.EP, X1.2 (GND), X1.4 (GND); also elsewhere on the board
unnamed: C114.1, R29.1, R30.2
unnamed: C118.1, C119.1, C120.1, C121.1, R31.1, R32.1, R33.1, R34.1, R38.2, R39.2
unnamed: D7.1, R37.1
unnamed: D9.1, R36.1
unnamed: Q1.3 (D), R37.2
unnamed: R40.1, S1.1
unnamed: R44.2, U1.56 (PA11)
unnamed: R23.1, R25.2, U5.A1 (IN+)
unnamed: R24.1, R25.1, U5.B1 (IN-)
unnamed: C66.1, C67.1, U6.21 (COM)
unnamed: C91.1, C92.1, U6.6 (MSV)
unnamed: C72.1, U6.19 (REF)
unnamed: C69.1, C70.1, C71.1, U6.20 (REF+)
unnamed: C68.1, C70.2, C71.2, U6.22 (REF-)
unnamed: C73.1, U6.18 (REFMS)
unnamed: C112.1, U7.11 (OUT1_N)
unnamed: C111.1, U7.12 (OUT1_P)
unnamed: C64.2, U8.9 (CP1)
unnamed: C64.1, U8.8 (CP2)
unnamed: C76.1, U8.7 (CP3)
unnamed: C77.1, U8.21 (CV3P3)
unnamed: R12.1, U8.45 (ICOM1), U8.49 (ICOM2), U8.50 (ISENSE)
unnamed: C115.1, C116.1, L1.1, U12.4 (VDD)

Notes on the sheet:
MOTOR CONTROL
LASER DRIVER
USB-C INPUT
TPIC2010
EPC21603
OPU DRIVER PCB
PMIC READ DATA
EPC5
MAX1304
CH569
HSPI Link MCU TX MCU RX HTCLK_1 => HRCLK_1 HTREQ_1 => HRACK_1 HTRDY_1 <= HTACK_1 HTVLD_1 => HRVLD_1 MCU_RX MCU_TX HRCLK_1 <= HTCLK_1 HRACK_1 <= HTREQ_1 HTACK_1 => HTRDY_1 HRVLD_1 <= HTVLD_1
CLK_GEN
USB to Parallel
LED INDICATORS
OPU CONNECTOR INPUT/OUTPUT
PMIC ALIGNMENT ADC
FPGA CONTROL
POWER_SUPPLY
MAX40025
Pull HD0(PA5) down to enter bootloader mode (Flash mode) USB shall enumerate for ISP(if no connection after 10s exit ISP)

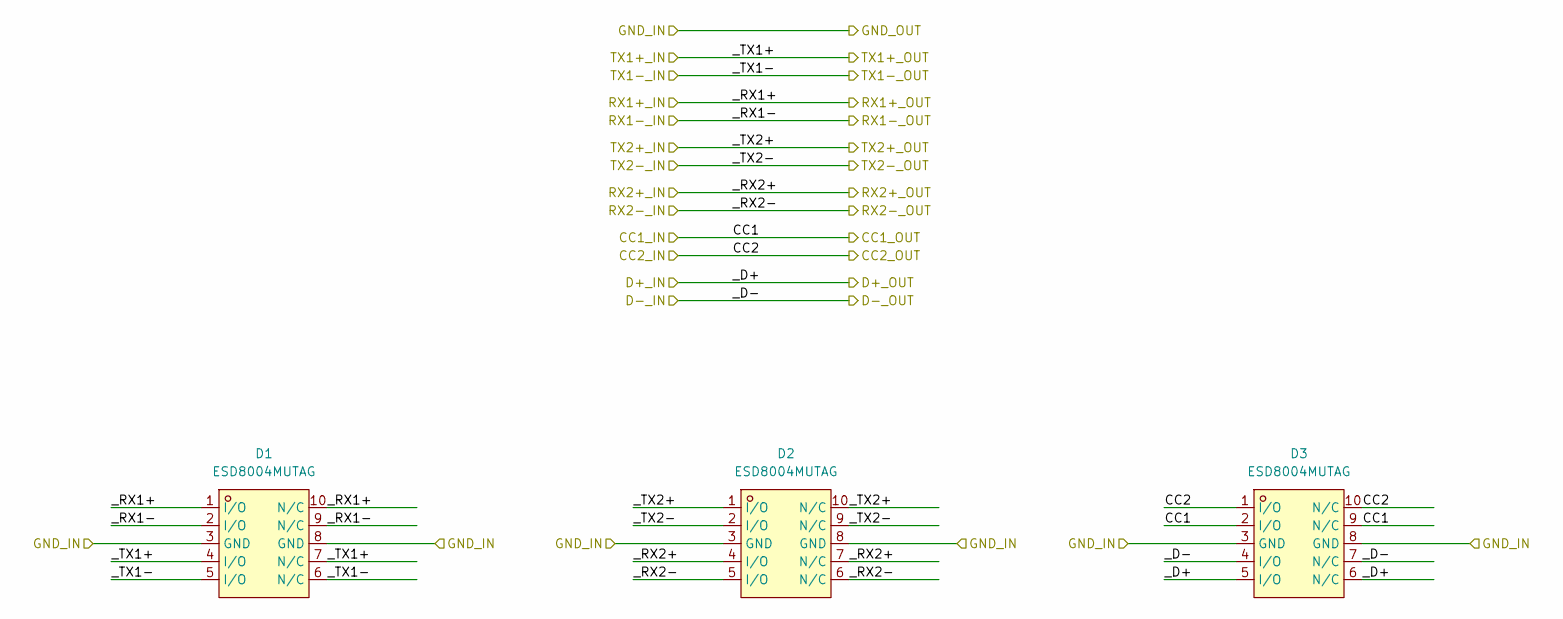
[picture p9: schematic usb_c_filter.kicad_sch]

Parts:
D1, D2, D3: ESD8004MUTAG; UDFN-10_L2.5-W1.0-P0.50-BL; LCSC Part C605399

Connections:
/CC1: D3.2 (I/O), D3.9 (N/C); also elsewhere on the board
/CC2: D3.1 (I/O), D3.10 (N/C); also elsewhere on the board
/D_+: D3.5 (I/O), D3.6 (N/C); also elsewhere on the board
/D_-: D3.4 (I/O), D3.7 (N/C); also elsewhere on the board
/RX1+: D1.1 (I/O), D1.10 (N/C); also elsewhere on the board
/RX1-: D1.2 (I/O), D1.9 (N/C); also elsewhere on the board
/RX2+: D2.4 (I/O), D2.7 (N/C); also elsewhere on the board
/RX2-: D2.5 (I/O), D2.6 (N/C); also elsewhere on the board
/TX1+: D1.4 (I/O), D1.7 (N/C); also elsewhere on the board
/TX1-: D1.5 (I/O), D1.6 (N/C); also elsewhere on the board
/TX2+: D2.1 (I/O), D2.10 (N/C); also elsewhere on the board
/TX2-: D2.2 (I/O), D2.9 (N/C); also elsewhere on the board
GND: D1.3 (GND), D1.8 (GND), D2.3 (GND), D2.8 (GND), D3.3 (GND), D3.8 (GND); also elsewhere on the board

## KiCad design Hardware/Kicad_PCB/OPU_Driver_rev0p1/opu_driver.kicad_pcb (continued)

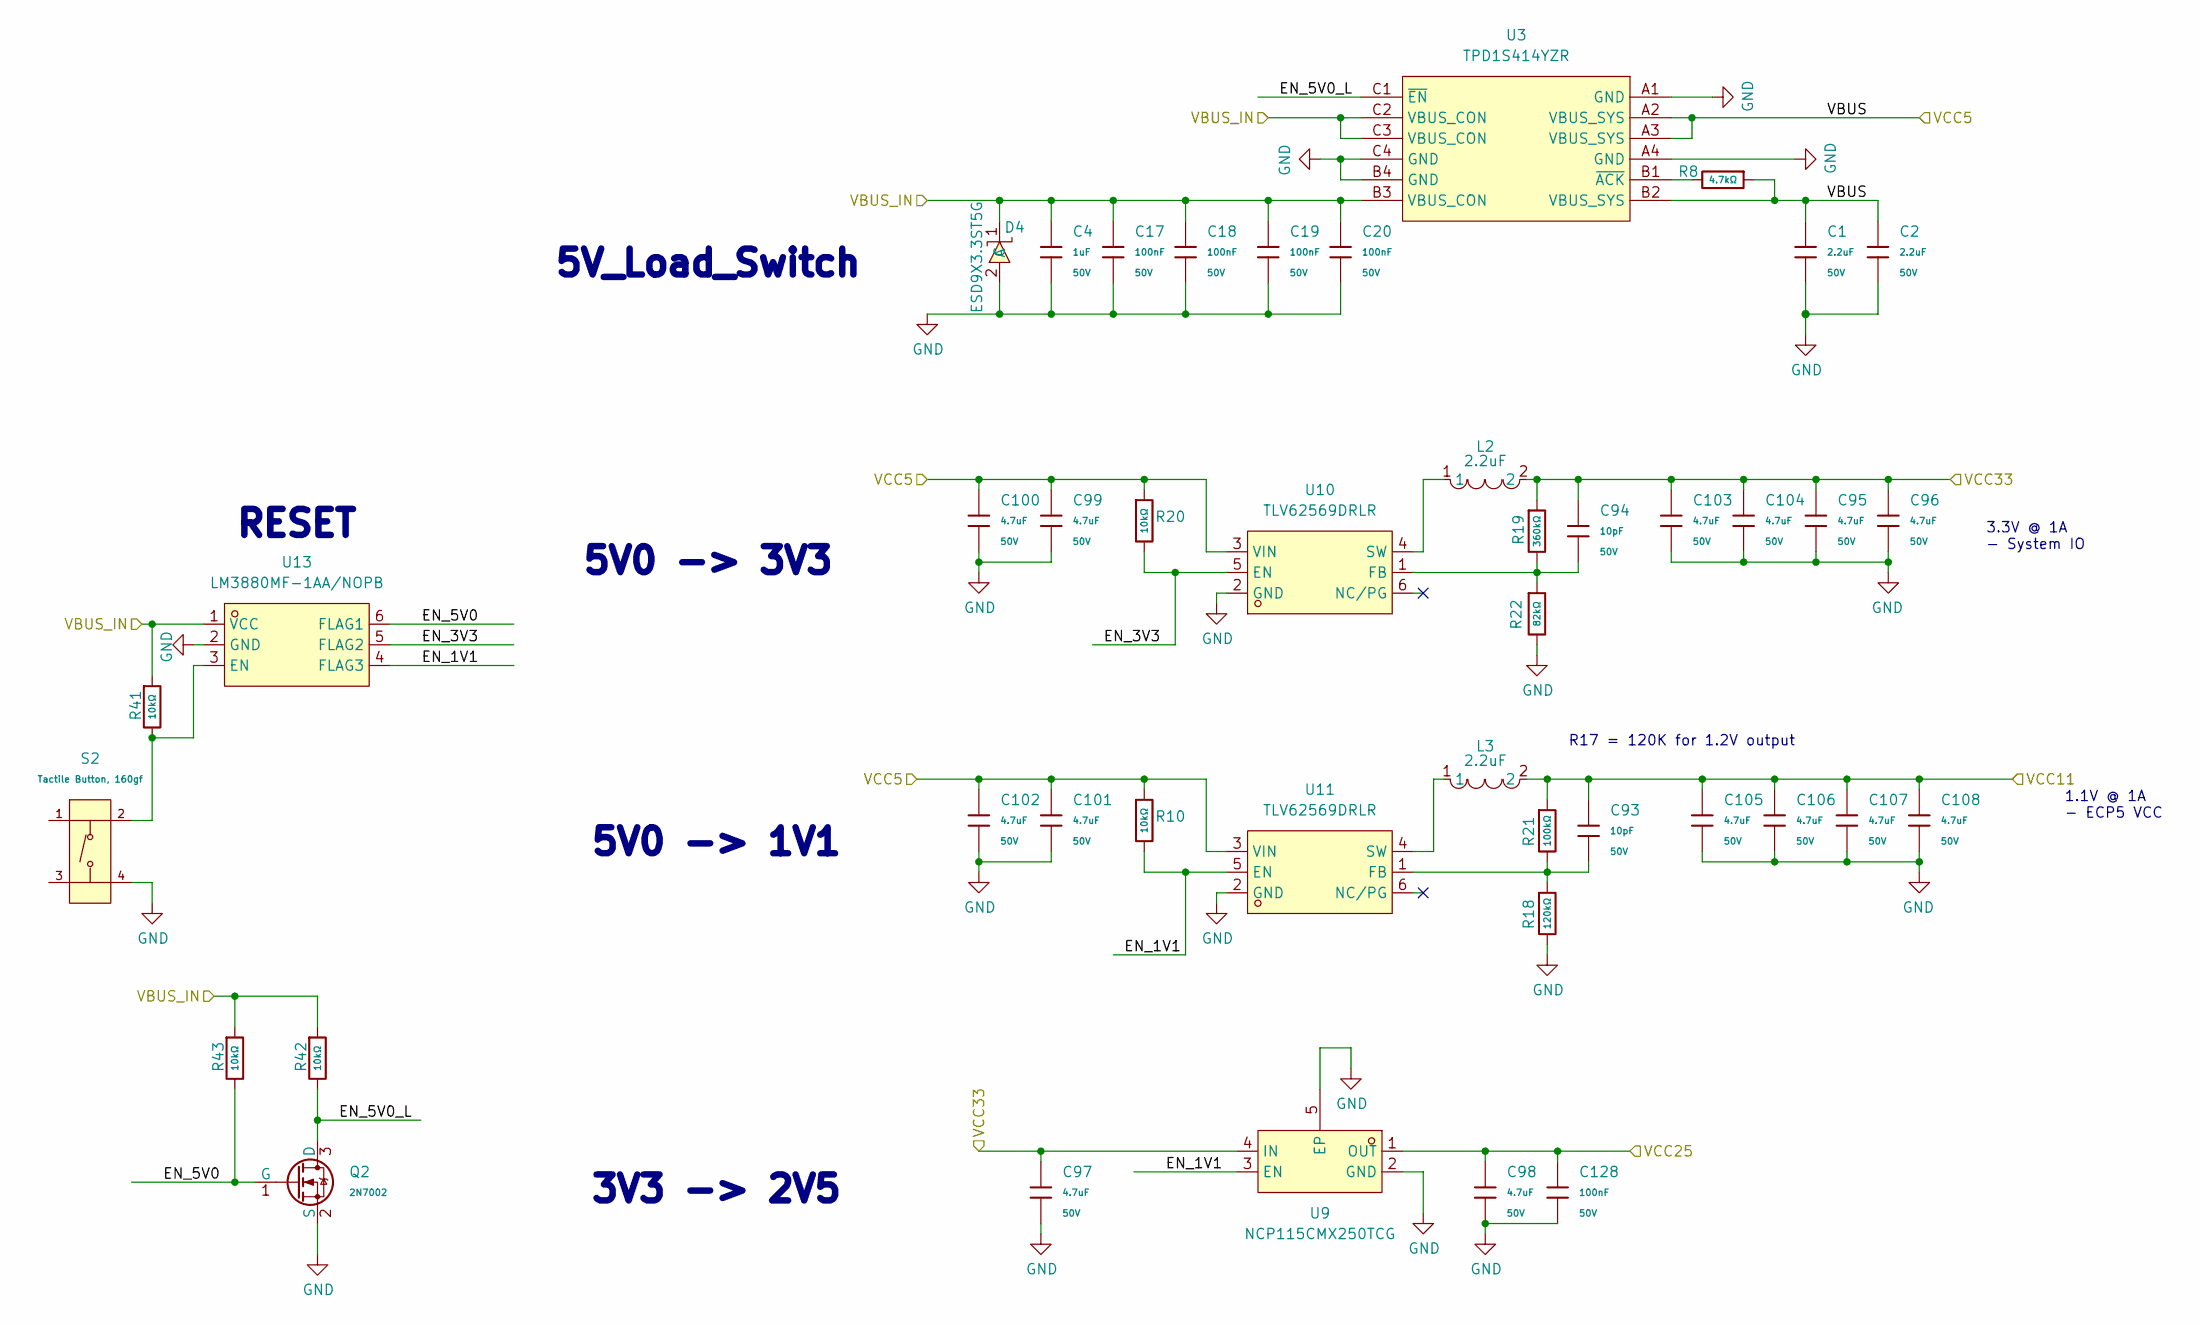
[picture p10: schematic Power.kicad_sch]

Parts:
C1, C2: 2.2uF; C_1206; Voltage Rated 50V; Tolerance ±10%; Part CL31B225KBHNNNE; LCSC C50254
C4: 1uF; C_0805; Voltage Rated 50V; Tolerance ±10%; Part CL21B105KBFNNNE; LCSC C28323
C17, C18, C19, C20, C128: 100nF; C_0402; Voltage Rated 50V; Tolerance ±10%; Part CL05B104KB54PNC; LCSC C307331
C93, C94: 10pF; C_0402; Voltage Rated 50V; Tolerance ±5%; Part CL05C100JB5NNNC; LCSC C32949
C95, C96, C97, C98, C99, C100, C101, C102, C103, C104, C105, C106, C107, C108: 4.7uF; C_1206; Voltage Rated 50V; Tolerance ±10%; Part 1206B475K500NT; LCSC C29823
D4: ESD9X3.3ST5G; SOD-923_L0.8-W0.6-LS1.0-RD; LCSC Part C130456
L2, L3: LQM21PN2R2NGCD; L0805; LCSC Part C86089
Q2: 2N7002; Q_SOT-23; Part 2N7002; LCSC C8545
R8: 4.7kΩ; R_0402; Overload Voltage (Max) 50V; Tolerance ±1%; Part 0402WGF4701TCE; LCSC C25900
R10, R20, R41, R42, R43: 10kΩ; R_0402; Overload Voltage (Max) 50V; Tolerance ±1%; Part 0402WGF1002TCE; LCSC C25744
R18: 120kΩ; R_0402; Overload Voltage (Max) 50V; Tolerance ±1%; Part 0402WGF1203TCE; LCSC C25750
R19: 360kΩ; R_0603; Overload Voltage (Max) 75V; Tolerance ±1%; Part 0603WAF3603T5E; LCSC C23146
R21: 100kΩ; R_0402; Overload Voltage (Max) 50V; Tolerance ±1%; Part 0402WGF1003TCE; LCSC C25741
R22: 82kΩ; R_0603; Overload Voltage (Max) 75V; Tolerance ±1%; Part 0603WAF8202T5E; LCSC C23254
S2: Tactile Button, 160gf; SW-SMD_4P-L5.1-W5.1-P3.70-LS6.5-TL-2; Voltage Rating (Dc) 12V; Part TS-1187A-B-A-B; LCSC C318884
U3: TPD1S414YZR; DSBGA-12_L1.9-W1.4-R3-C4-P0.40-TL; LCSC Part C411873
U9: NCP115CMX250TCG; XDFN-4_L1.0-W1.0-P0.65-BL-EP; LCSC Part C603508
U10, U11: TLV62569DRLR; SOT-563_L1.6-W1.2-P0.50-LS1.6-BL; LCSC Part C163217
U13: LM3880MF-1AA/NOPB; SOT-23-6_L2.9-W1.6-P0.95-LS2.8-BR; LCSC Part C486059

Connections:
+1V1: C93.1, C105.1, C106.1, C107.1, C108.1, L3.2, R21.1; also elsewhere on the board
+2V5: C98.1, C128.1, U9.1 (OUT); also elsewhere on the board
+3V3: C94.1, C95.1, C96.1, C97.1, C103.1, C104.1, L2.2, R19.1, U9.4 (IN); also elsewhere on the board
/Power/EN_1V1: R10.2, U9.3 (EN), U11.5 (EN), U13.4 (FLAG3)
/Power/EN_3V3: R20.2, U10.5 (EN), U13.5 (FLAG2)
/Power/EN_5V0: Q2.1 (G), R43.2, U13.6 (FLAG1)
/Power/EN_5V0_L: Q2.3 (D), R42.2, U3.C1 (~EN)
/VBUS: C4.1, C17.1, C18.1, C19.1, C20.1, D4.1 (C), R41.1, R42.1, R43.1, U3.B3 (VBUS_CON), U3.C2 (VBUS_CON), U3.C3 (VBUS_CON), U13.1 (VCC); also elsewhere on the board
GND: C1.2, C2.2, C4.2, C17.2, C18.2, C19.2, C20.2, C95.2, C96.2, C97.2, C98.2, C99.2, C100.2, C101.2, C102.2, C103.2, C104.2, C105.2, C106.2, C107.2, C108.2, C128.2, D4.2 (A), Q2.2 (S), R18.2, R22.2, S2.4 (D), U3.A1 (GND), U3.A4 (GND), U3.B4 (GND), U3.C4 (GND), U9.2 (GND), U9.5 (EP), U10.2 (GND), U11.2 (GND), U13.2 (GND); also elsewhere on the board
unnamed: R41.2, S2.2 (B), U13.3 (EN)
unnamed: R8.2, U3.B1 (~ACK)
unnamed: C94.2, R19.2, R22.1, U10.1 (FB)
unnamed: L2.1, U10.4 (SW)
unnamed: C93.2, R18.1, R21.2, U11.1 (FB)
unnamed: L3.1, U11.4 (SW)

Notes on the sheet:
3.3V @ 1A - System IO
5V0 -> 1V1
RESET
5V_Load_Switch
1.1V @ 1A - ECP5 VCC
5V0 -> 3V3
3V3 -> 2V5
R17 = 120K for 1.2V output

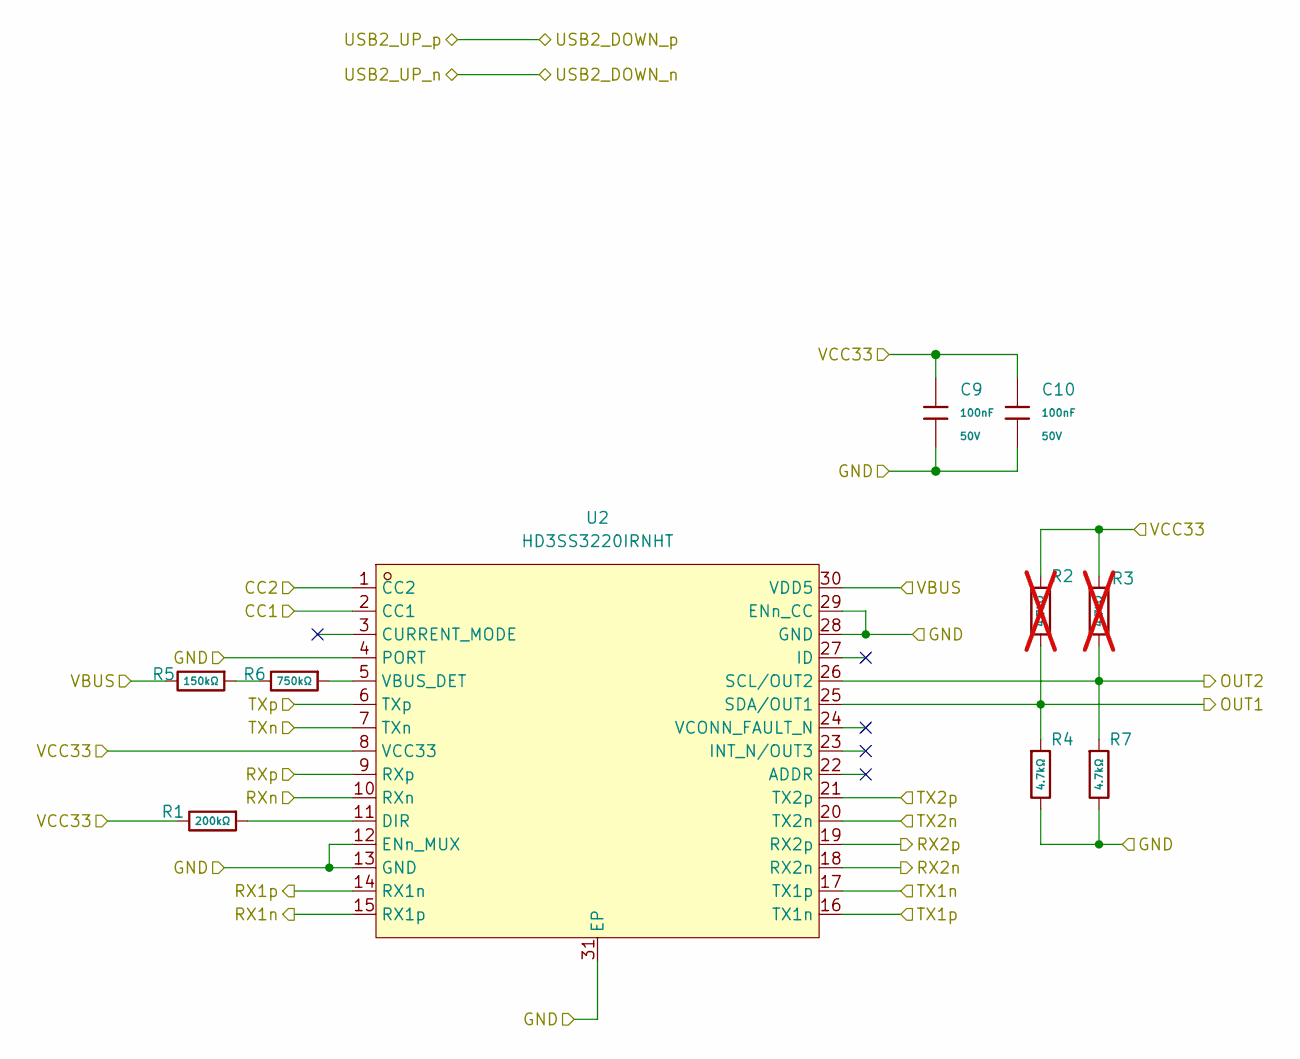
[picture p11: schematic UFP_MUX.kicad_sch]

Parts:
C9, C10: 100nF; C_0402; Voltage Rated 50V; Tolerance ±10%; Part CL05B104KB54PNC; LCSC C307331
R1: 200kΩ; R_0402; Overload Voltage (Max) 50V; Tolerance ±1%; Part 0402WGF2003TCE; LCSC C25764
R2, R3: 4.7kΩ; R_0402; Overload Voltage (Max) 50V; Tolerance ±1%; Part 0402WGF4701TCE; LCSC C25900; not fitted
R4, R7: 4.7kΩ; R_0402; Overload Voltage (Max) 50V; Tolerance ±1%; Part 0402WGF4701TCE; LCSC C25900
R5: 150kΩ; R_0402; Overload Voltage (Max) 50V; Tolerance ±1%; Part 0402WGF1503TCE; LCSC C25755
R6: 750kΩ; R_0603; Overload Voltage (Max) 75V; Tolerance ±1%; Part 0603WAF7503T5E; LCSC C23240
U2: HD3SS3220IRNHT; WQFN-30_L4.5-W2.5-P0.4-BL-EP; LCSC Part C2876685

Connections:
+3V3: C9.1, C10.1, R1.2, R2.1, R3.1, U2.8 (VCC33); also elsewhere on the board
/CC1: U2.2 (CC1); also elsewhere on the board
/CC2: U2.1 (CC2); also elsewhere on the board
/RX1+: U2.14 (RX1n); also elsewhere on the board
/RX1-: U2.15 (RX1p); also elsewhere on the board
/RX2+: U2.19 (RX2p); also elsewhere on the board
/RX2-: U2.18 (RX2n); also elsewhere on the board
/RXN: U2.10 (RXn); also elsewhere on the board
/RXP: U2.9 (RXp); also elsewhere on the board
/TX1_N: U2.17 (TX1p); also elsewhere on the board
/TX1_P: U2.16 (TX1n); also elsewhere on the board
/TX2_N: U2.20 (TX2n); also elsewhere on the board
/TX2_P: U2.21 (TX2p); also elsewhere on the board
/TXpre_N: U2.7 (TXn); also elsewhere on the board
/TXpre_P: U2.6 (TXp); also elsewhere on the board
/UFP_MUX/OUT1: R2.2, R4.1, U2.25 (SDA/OUT1)
/UFP_MUX/OUT2: R3.2, R7.1, U2.26 (SCL/OUT2)
GND: C9.2, C10.2, R4.2, R7.2, U2.4 (PORT), U2.12 (ENn_MUX), U2.13 (GND), U2.28 (GND), U2.29 (ENn_CC), U2.31 (EP); also elsewhere on the board
unnamed: R5.1, R6.2
unnamed: R1.1, U2.11 (DIR)
unnamed: R6.1, U2.5 (VBUS_DET)

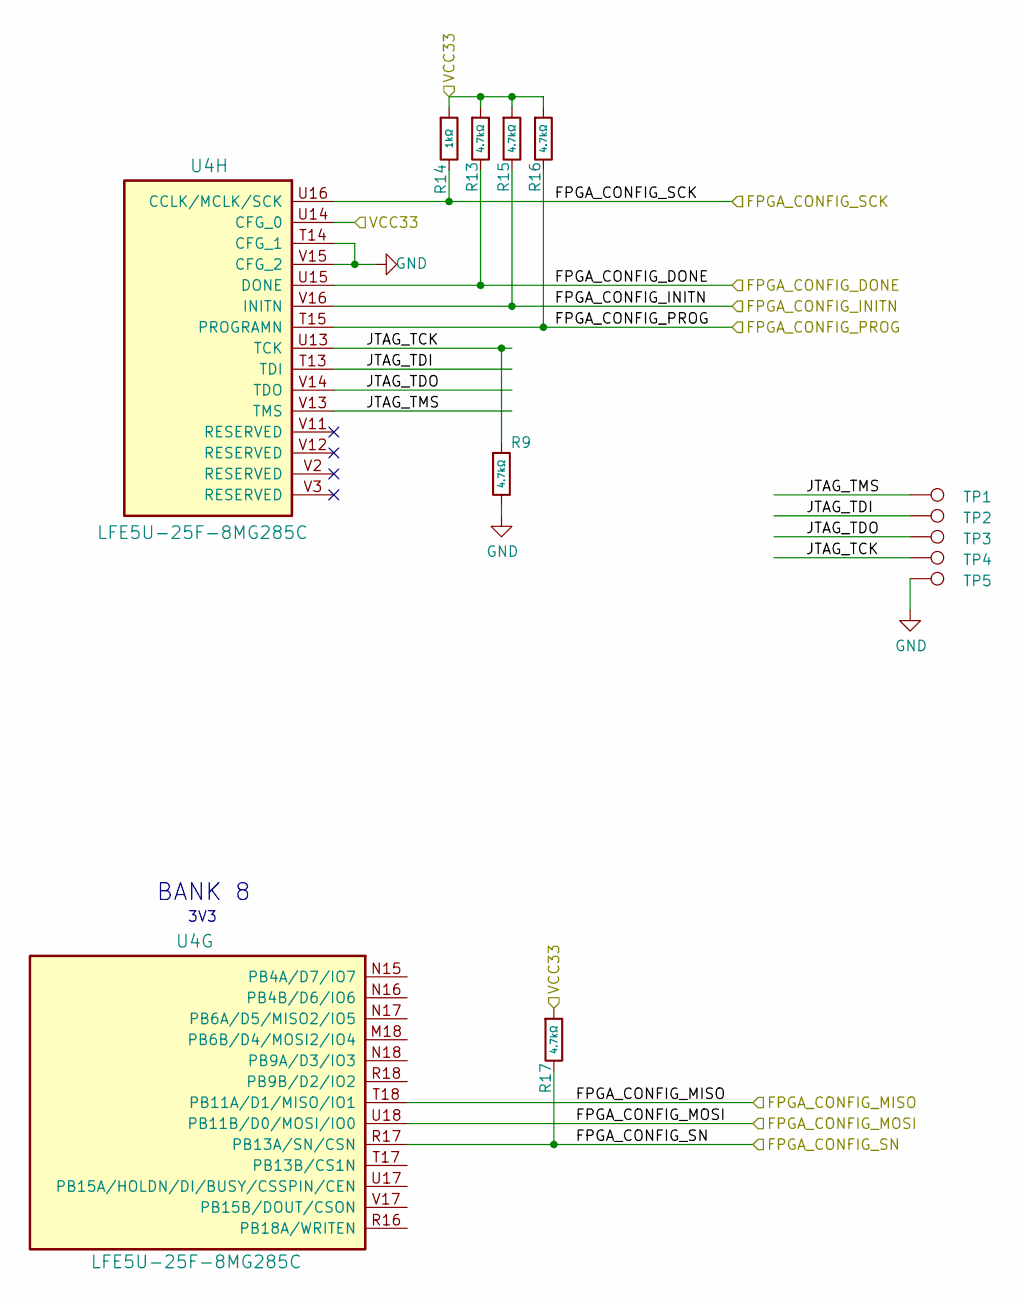
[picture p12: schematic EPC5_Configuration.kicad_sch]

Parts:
R9, R13, R15, R16, R17: 4.7kΩ; R_0402; Overload Voltage (Max) 50V; Tolerance ±1%; Part 0402WGF4701TCE; LCSC C25900
R14: 1kΩ; R_0402; Overload Voltage (Max) 50V; Tolerance ±1%; Part 0402WGF1001TCE; LCSC C11702
TP1, TP2, TP3, TP4, TP5: TestPoint; TestPoint_Pad_D1.0mm
U4: LFE5U-25F-8MG285C; csBGA285

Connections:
+3V3: R13.1, R14.1, R15.1, R16.1, R17.1, U4.U14 (CFG_0); also elsewhere on the board
/EPC5_Configuration/JTAG_TCK: R9.1, TP4.1, U4.U13 (TCK)
/EPC5_Configuration/JTAG_TDI: TP2.1, U4.T13 (TDI)
/EPC5_Configuration/JTAG_TDO: TP3.1, U4.V14 (TDO)
/EPC5_Configuration/JTAG_TMS: TP1.1, U4.V13 (TMS)
/FPGA_CONFIG_DONE: R13.2, U4.U15 (DONE); also elsewhere on the board
/FPGA_CONFIG_INITN: R15.2, U4.V16 (INITN); also elsewhere on the board
/FPGA_CONFIG_MISO: U4.T18 (PB11A/D1/MISO/IO1); also elsewhere on the board
/FPGA_CONFIG_MOSI: U4.U18 (PB11B/D0/MOSI/IO0); also elsewhere on the board
/FPGA_CONFIG_PROG: R16.2, U4.T15 (PROGRAMN); also elsewhere on the board
/FPGA_CONFIG_SCK: R14.2, U4.U16 (CCLK/MCLK/SCK); also elsewhere on the board
/FPGA_CONFIG_SN: R17.2, U4.R17 (PB13A/SN/CSN); also elsewhere on the board
GND: R9.2, TP5.1, U4.T14 (CFG_1), U4.V15 (CFG_2); also elsewhere on the board

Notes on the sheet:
BANK 8
3V3

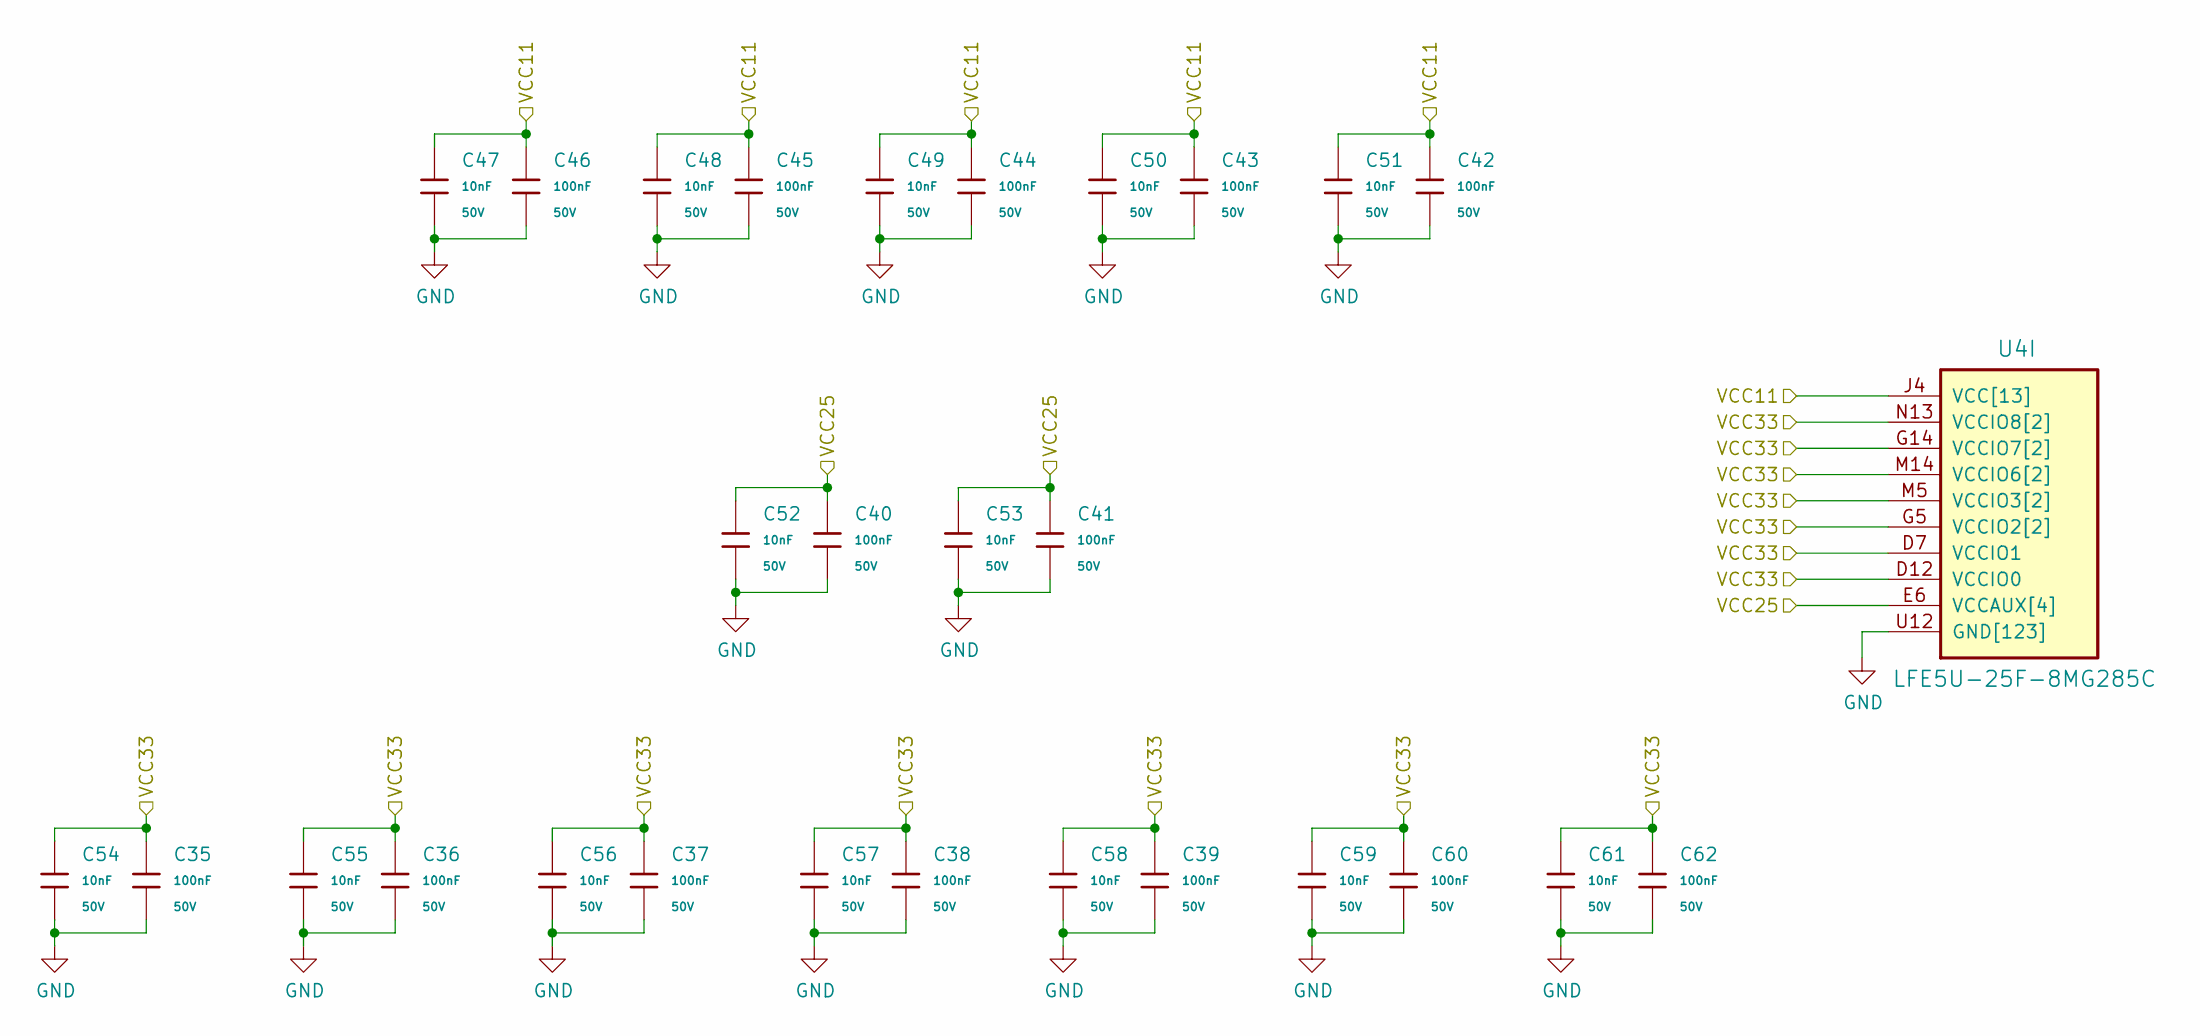
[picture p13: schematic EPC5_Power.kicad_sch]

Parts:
C35, C36, C37, C38, C39, C40, C41, C42, C43, C44, C45, C46, C60, C62: 100nF; C_0402; Voltage Rated 50V; Tolerance ±10%; Part CL05B104KB54PNC; LCSC C307331
C47, C48, C49, C50, C51, C52, C53, C54, C55, C56, C57, C58, C59, C61: 10nF; C_0402; Voltage Rated 50V; Tolerance ±10%; Part CL05B103KB5NNNC; LCSC C15195
U4: LFE5U-25F-8MG285C; csBGA285

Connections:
+1V1: C42.1, C43.1, C44.1, C45.1, C46.1, C47.1, C48.1, C49.1, C50.1, C51.1, U4.D8 (VCC[13]), U4.D9 (VCC[13]), U4.D10 (VCC[13]), U4.D11 (VCC[13]), U4.J4 (VCC[13]), U4.J5 (VCC[13]), U4.J14 (VCC[13]), U4.J15 (VCC[13]), U4.M4 (VCC[13]), U4.M15 (VCC[13]), U4.P7 (VCC[13]), U4.P9 (VCC[13]), U4.P11 (VCC[13]); also elsewhere on the board
+2V5: C40.1, C41.1, C52.1, C53.1, U4.E6 (VCCAUX[4]), U4.E13 (VCCAUX[4]), U4.N6 (VCCAUX[4]), U4.P13 (VCCAUX[4]); also elsewhere on the board
+3V3: C35.1, C36.1, C37.1, C38.1, C39.1, C54.1, C55.1, C56.1, C57.1, C58.1, C59.1, C60.1, C61.1, C62.1, U4.D7 (VCCIO1), U4.D12 (VCCIO0), U4.G5 (VCCIO2[2]), U4.G14 (VCCIO7[2]), U4.H5 (VCCIO2[2]), U4.H14 (VCCIO7[2]), U4.M5 (VCCIO3[2]), U4.M14 (VCCIO6[2]), U4.N5 (VCCIO3[2]), U4.N13 (VCCIO8[2]), U4.N14 (VCCIO6[2]), U4.P14 (VCCIO8[2]); also elsewhere on the board
GND: C35.2, C36.2, C37.2, C38.2, C39.2, C40.2, C41.2, C42.2, C43.2, C44.2, C45.2, C46.2, C47.2, C48.2, C49.2, C50.2, C51.2, C52.2, C53.2, C54.2, C55.2, C56.2, C57.2, C58.2, C59.2, C60.2, C61.2, C62.2, U4.B3 (GND[123]), U4.B16 (GND[123]), U4.E5 (GND[123]), U4.E7 (GND[123]), U4.E8 (GND[123]), U4.E9 (GND[123]), U4.E10 (GND[123]), U4.E11 (GND[123]), U4.E12 (GND[123]), U4.E14 (GND[123]), U4.F5 (GND[123]), U4.F6 (GND[123]), U4.F7 (GND[123]), U4.F8 (GND[123]), U4.F9 (GND[123]), U4.F10 (GND[123]), U4.F11 (GND[123]), U4.F12 (GND[123]), U4.F13 (GND[123]), U4.F14 (GND[123]), U4.G2 (GND[123]), U4.G6 (GND[123]), U4.G7 (GND[123]), U4.G8 (GND[123]), U4.G9 (GND[123]), U4.G10 (GND[123]), U4.G11 (GND[123]), U4.G12 (GND[123]), U4.G13 (GND[123]), U4.G17 (GND[123]), U4.H6 (GND[123]), U4.H7 (GND[123]), U4.H8 (GND[123]), U4.H9 (GND[123]), U4.H10 (GND[123]), U4.H11 (GND[123]), U4.H12 (GND[123]), U4.H13 (GND[123]), U4.J6 (GND[123]), U4.J7 (GND[123]), U4.J8 (GND[123]), U4.J9 (GND[123]), U4.J10 (GND[123]), U4.J11 (GND[123]), U4.J12 (GND[123]), U4.J13 (GND[123]), U4.K5 (GND[123]), U4.K6 (GND[123]), U4.K7 (GND[123]), U4.K8 (GND[123]), U4.K9 (GND[123]), U4.K10 (GND[123]), U4.K11 (GND[123]), U4.K12 (GND[123]), U4.K13 (GND[123]), U4.K14 (GND[123]), U4.L2 (GND[123]), U4.L5 (GND[123]), U4.L6 (GND[123]), U4.L7 (GND[123]), U4.L8 (GND[123]), U4.L9 (GND[123]), U4.L10 (GND[123]), U4.L11 (GND[123]), U4.L12 (GND[123]), U4.L13 (GND[123]), U4.L14 (GND[123]), U4.L17 (GND[123]), U4.M6 (GND[123]), U4.M7 (GND[123]), U4.M8 (GND[123]), U4.M9 (GND[123]), U4.M10 (GND[123]), U4.M11 (GND[123]), U4.M12 (GND[123]), U4.M13 (GND[123]), U4.N7 (GND[123]), U4.N8 (GND[123]), U4.N9 (GND[123]), U4.N10 (GND[123]), U4.N11 (GND[123]), U4.N12 (GND[123]), U4.P5 (GND[123]), U4.P6 (GND[123]), U4.P8 (GND[123]), U4.P10 (GND[123]), U4.P12 (GND[123]), U4.R1 (GND[123]), U4.R2 (GND[123]), U4.R3 (GND[123]), U4.R10 (GND[123]), U4.T1 (GND[123]), U4.T2 (GND[123]), U4.T3 (GND[123]), U4.T4 (GND[123]), U4.T5 (GND[123]), U4.T6 (GND[123]), U4.T7 (GND[123]), U4.T8 (GND[123]), U4.T9 (GND[123]), U4.T10 (GND[123]), U4.T11 (GND[123]), U4.T12 (GND[123]), U4.T16 (GND[123]), U4.U1 (GND[123]), U4.U2 (GND[123]), U4.U3 (GND[123]), U4.U4 (GND[123]), U4.U5 (GND[123]), U4.U6 (GND[123]), U4.U7 (GND[123]), U4.U8 (GND[123]), U4.U9 (GND[123]), U4.U10 (GND[123]), U4.U11 (GND[123]), U4.U12 (GND[123]), U4.V4 (GND[123]), U4.V5 (GND[123]), U4.V6 (GND[123]), U4.V7 (GND[123]), U4.V8 (GND[123]), U4.V9 (GND[123]), U4.V10 (GND[123]); also elsewhere on the board

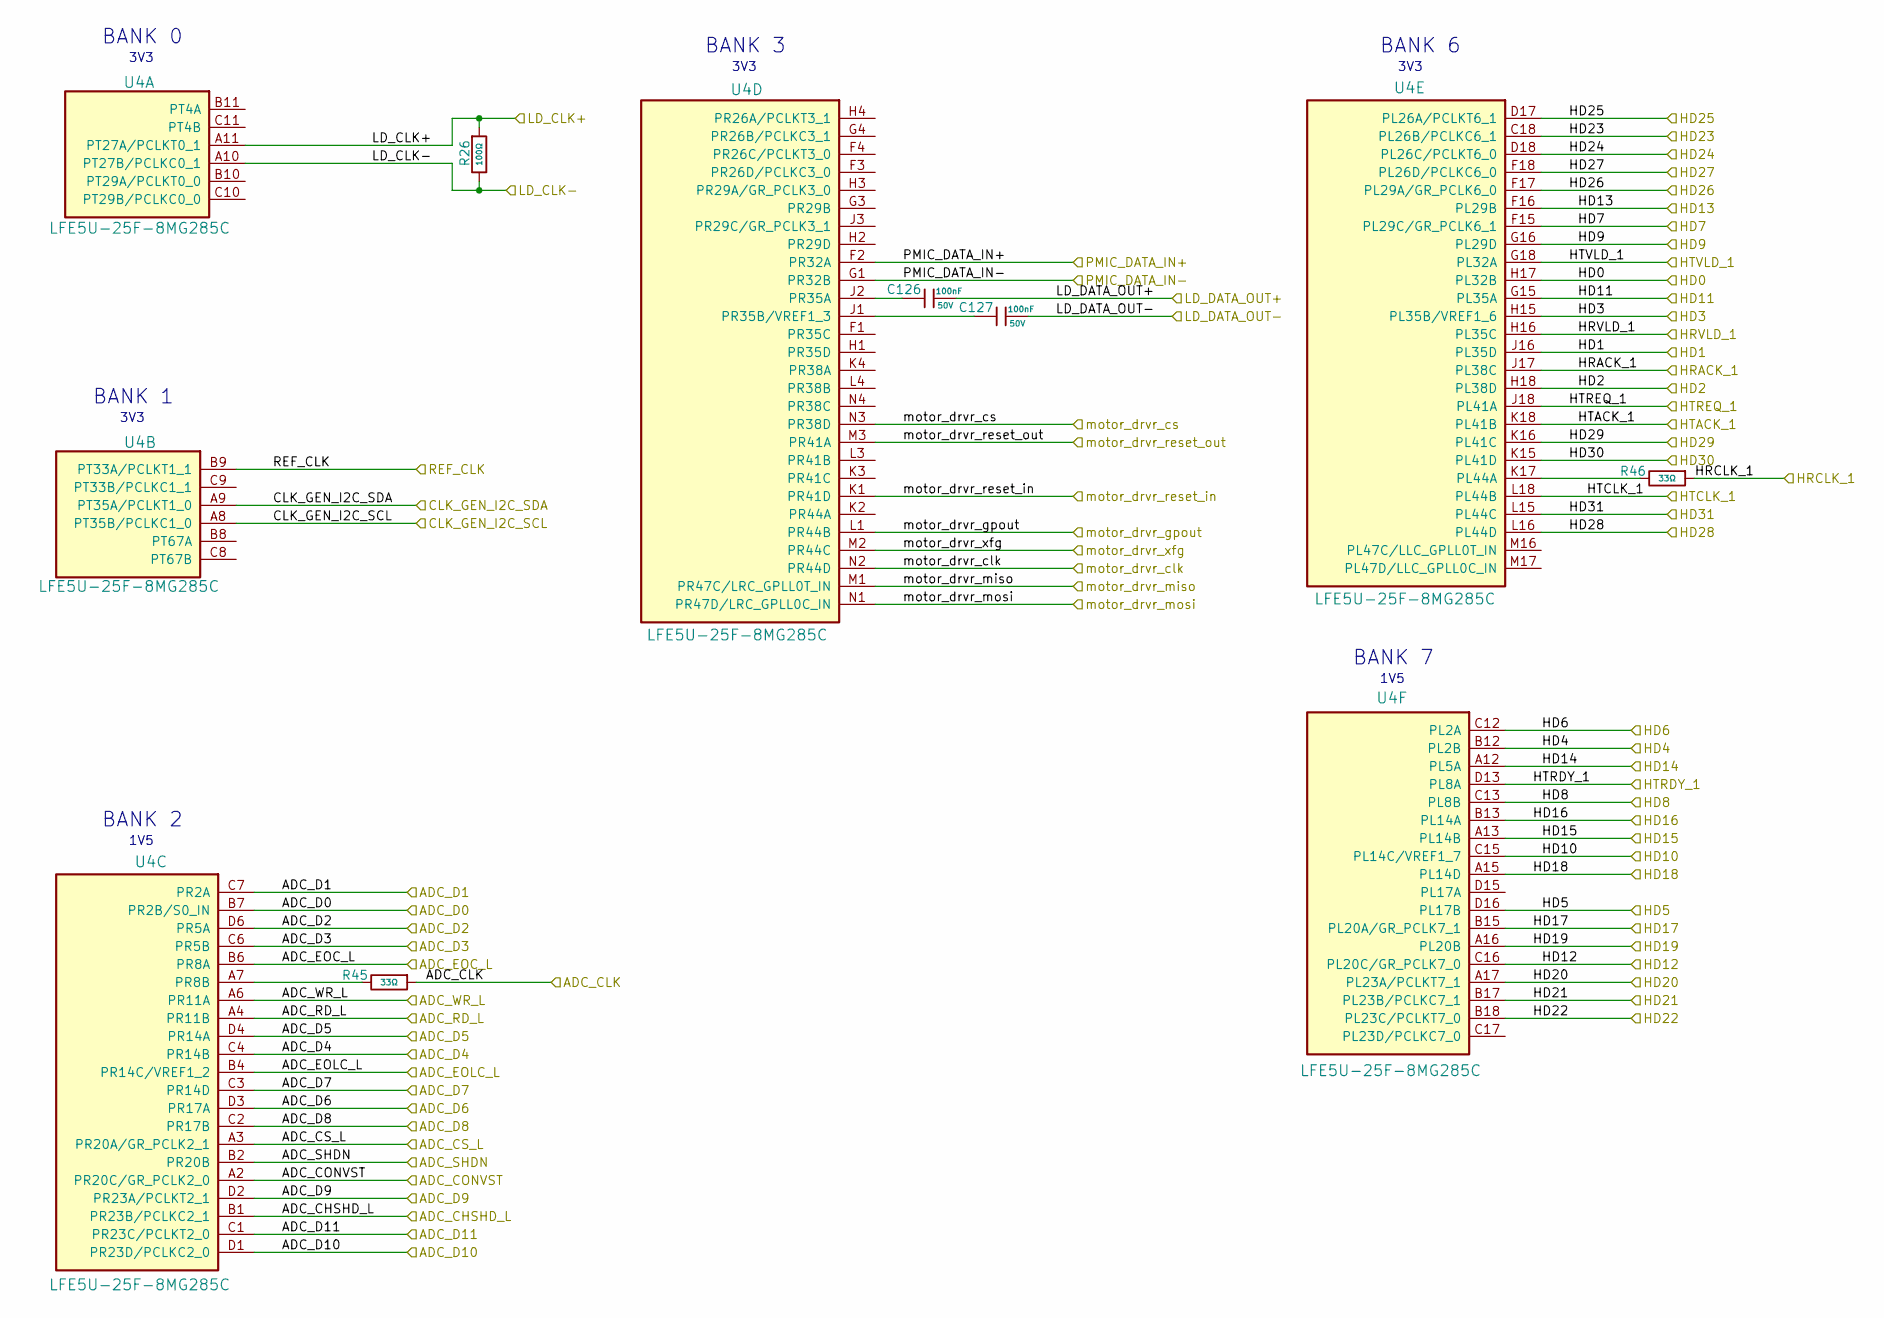
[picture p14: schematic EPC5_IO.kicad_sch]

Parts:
C126, C127: 100nF; C_0402; Voltage Rated 50V; Tolerance ±10%; Part CL05B104KB54PNC; LCSC C307331
R26: 100Ω; R_0402; Overload Voltage (Max) 50V; Tolerance ±1%; Part 0402WGF1000TCE; LCSC C25076
R45, R46: 33Ω; R_0402; Overload Voltage (Max) 50V; Tolerance ±1%; Part 0402WGF330JTCE; LCSC C25105
U4: LFE5U-25F-8MG285C; csBGA285

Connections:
/ADC_CHSHD_L: U4.B1 (PR23B/PCLKC2_1); also elsewhere on the board
/ADC_CLK: R45.1; also elsewhere on the board
/ADC_CONVST: U4.A2 (PR20C/GR_PCLK2_0); also elsewhere on the board
/ADC_CS_L: U4.A3 (PR20A/GR_PCLK2_1); also elsewhere on the board
/ADC_D0: U4.B7 (PR2B/S0_IN); also elsewhere on the board
/ADC_D1: U4.C7 (PR2A); also elsewhere on the board
/ADC_D2: U4.D6 (PR5A); also elsewhere on the board
/ADC_D3: U4.C6 (PR5B); also elsewhere on the board
/ADC_D4: U4.C4 (PR14B); also elsewhere on the board
/ADC_D5: U4.D4 (PR14A); also elsewhere on the board
/ADC_D6: U4.D3 (PR17A); also elsewhere on the board
/ADC_D7: U4.C3 (PR14D); also elsewhere on the board
/ADC_D8: U4.C2 (PR17B); also elsewhere on the board
/ADC_D9: U4.D2 (PR23A/PCLKT2_1); also elsewhere on the board
/ADC_D10: U4.D1 (PR23D/PCLKC2_0); also elsewhere on the board
/ADC_D11: U4.C1 (PR23C/PCLKT2_0); also elsewhere on the board
/ADC_EOC_L: U4.B6 (PR8A); also elsewhere on the board
/ADC_EOLC_L: U4.B4 (PR14C/VREF1_2); also elsewhere on the board
/ADC_RD_L: U4.A4 (PR11B); also elsewhere on the board
/ADC_SHDN: U4.B2 (PR20B); also elsewhere on the board
/ADC_WR_L: U4.A6 (PR11A); also elsewhere on the board
/CLK_GEN_I2C_SCL: U4.A8 (PT35B/PCLKC1_0); also elsewhere on the board
/CLK_GEN_I2C_SDA: U4.A9 (PT35A/PCLKT1_0); also elsewhere on the board
/HD0: U4.H17 (PL32B); also elsewhere on the board
/HD1: U4.J16 (PL35D); also elsewhere on the board
/HD2: U4.H18 (PL38D); also elsewhere on the board
/HD3: U4.H15 (PL35B/VREF1_6); also elsewhere on the board
/HD4: U4.B12 (PL2B); also elsewhere on the board
/HD5: U4.D16 (PL17B); also elsewhere on the board
/HD6: U4.C12 (PL2A); also elsewhere on the board
/HD7: U4.F15 (PL29C/GR_PCLK6_1); also elsewhere on the board
/HD8: U4.C13 (PL8B); also elsewhere on the board
/HD9: U4.G16 (PL29D); also elsewhere on the board
/HD10: U4.C15 (PL14C/VREF1_7); also elsewhere on the board
/HD11: U4.G15 (PL35A); also elsewhere on the board
/HD12: U4.C16 (PL20C/GR_PCLK7_0); also elsewhere on the board
/HD13: U4.F16 (PL29B); also elsewhere on the board
/HD14: U4.A12 (PL5A); also elsewhere on the board
/HD15: U4.A13 (PL14B); also elsewhere on the board
/HD16: U4.B13 (PL14A); also elsewhere on the board
/HD17: U4.B15 (PL20A/GR_PCLK7_1); also elsewhere on the board
/HD18: U4.A15 (PL14D); also elsewhere on the board
/HD19: U4.A16 (PL20B); also elsewhere on the board
/HD20: U4.A17 (PL23A/PCLKT7_1); also elsewhere on the board
/HD21: U4.B17 (PL23B/PCLKC7_1); also elsewhere on the board
/HD22: U4.B18 (PL23C/PCLKT7_0); also elsewhere on the board
/HD23: U4.C18 (PL26B/PCLKC6_1); also elsewhere on the board
/HD24: U4.D18 (PL26C/PCLKT6_0); also elsewhere on the board
/HD25: U4.D17 (PL26A/PCLKT6_1); also elsewhere on the board
/HD26: U4.F17 (PL29A/GR_PCLK6_0); also elsewhere on the board
/HD27: U4.F18 (PL26D/PCLKC6_0); also elsewhere on the board
/HD28: U4.L16 (PL44D); also elsewhere on the board
/HD29: U4.K16 (PL41C); also elsewhere on the board
/HD30: U4.K15 (PL41D); also elsewhere on the board
/HD31: U4.L15 (PL44C); also elsewhere on the board
/HRACK_1: U4.J17 (PL38C); also elsewhere on the board
/HRCLK_1: R46.1; also elsewhere on the board
/HRVLD_1: U4.H16 (PL35C); also elsewhere on the board
/HTACK_1: U4.K18 (PL41B); also elsewhere on the board
/HTCLK_1: U4.L18 (PL44B); also elsewhere on the board
/HTRDY_1: U4.D13 (PL8A); also elsewhere on the board
/HTREQ_1: U4.J18 (PL41A); also elsewhere on the board
/HTVLD_1: U4.G18 (PL32A); also elsewhere on the board
/LD_CLK+: R26.1, U4.A11 (PT27A/PCLKT0_1); also elsewhere on the board
/LD_CLK-: R26.2, U4.A10 (PT27B/PCLKC0_1); also elsewhere on the board
/LD_DATA_OUT+: C126.2; also elsewhere on the board
/LD_DATA_OUT-: C127.2; also elsewhere on the board
/PMIC_DATA_IN+: U4.F2 (PR32A); also elsewhere on the board
/PMIC_DATA_IN-: U4.G1 (PR32B); also elsewhere on the board
/motor_drvr_clk: U4.N2 (PR44D); also elsewhere on the board
/motor_drvr_cs: U4.N3 (PR38D); also elsewhere on the board
/motor_drvr_gpout: U4.L1 (PR44B); also elsewhere on the board
/motor_drvr_miso: U4.M1 (PR47C/LRC_GPLL0T_IN); also elsewhere on the board
/motor_drvr_mosi: U4.N1 (PR47D/LRC_GPLL0C_IN); also elsewhere on the board
/motor_drvr_reset_in: U4.K1 (PR41D); also elsewhere on the board
/motor_drvr_reset_out: U4.M3 (PR41A); also elsewhere on the board
/motor_drvr_xfg: U4.M2 (PR44C); also elsewhere on the board
/ref_clk: U4.B9 (PT33A/PCLKT1_1); also elsewhere on the board
unnamed: R45.2, U4.A7 (PR8B)
unnamed: C126.1, U4.J2 (PR35A)
unnamed: C127.1, U4.J1 (PR35B/VREF1_3)
unnamed: R46.2, U4.K17 (PL44A)

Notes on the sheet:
BANK 2
BANK 1
BANK 7
3V3
1V5
3V3
BANK 6
BANK 0
BANK 3

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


Board: 4 copper layers, 50.0 x 73.5 mm, 218 parts (99 on the bottom side), 193 nets.

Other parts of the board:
C7#2: 10pF; C_0402
C8#2: 100nF; C_0402

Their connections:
GND: C7#2.2, C8#2.2; also elsewhere on the board
